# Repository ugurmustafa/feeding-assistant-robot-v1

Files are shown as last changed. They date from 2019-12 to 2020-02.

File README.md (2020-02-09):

# Feeding Assistant Robot
This repository contains all related documents and files about Feeding Assistant Robot project. This project is being held for the Senior Design Project course at Mechatronics Engineering Department at Yildiz Technical University, Istanbul, Turkey. Also, this project is advised by Prof. Erhan Akdogan at Biomechatronics Laboratory.

Currently, our team consists of four senior Mechatronics Engineering students: [Mustafa UGUR](https://www.linkedin.com/in/mustafa-uğur-41b13310a), [Oguzhan YARDIMCI](https://www.linkedin.com/in/oguzhan-yardimci-505118144), [Cemil YILMAZ](https://www.linkedin.com/in/cemil-yılmaz-664a7b13b) and [Haluk BASI](https://www.linkedin.com/in/haluk-başı-9a2321143).

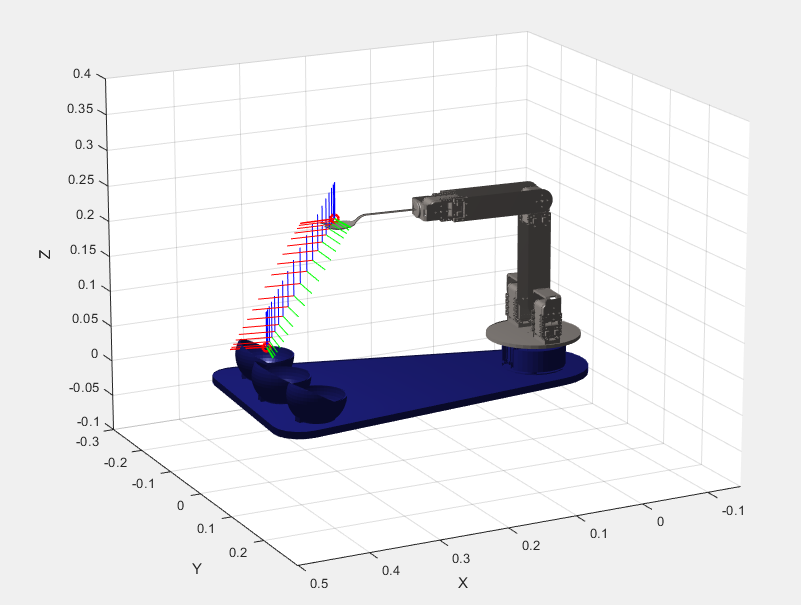
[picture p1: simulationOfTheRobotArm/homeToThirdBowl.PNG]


To see the files related with the simulation of the robot arm go to the file [simulationOfTheRobotArm](https://github.com/Ugurmustafa97/FeedingAssistantRobot/tree/master/simulationOfTheRobotArm).

To run simulation files for the trajectory planning go to  the directory [simulationOfTheRobotArm/filesForSimulation/urdf/matlabFiles/](https://github.com/Ugurmustafa97/FeedingAssistantRobot/tree/master/simulationOfTheRobotArm/filesForSimulation/urdf/matlabFiles)

To run simulation files for the dynamic analyses of the robot arm go to  the directory [simulationOfTheRobotArm/filesForController](https://github.com/Ugurmustafa97/FeedingAssistantRobot/tree/master/simulationOfTheRobotArm/filesForSimulation/urdf/matlabFiles)

To see the files realated with the mout tacking algorithm go to the file [mouthTrackingAlgorithm](https://github.com/Ugurmustafa97/FeedingAssistantRobot/tree/master/mouthTrackingAlgorithm)

To see the whole CAD files go to the [CADFiles](https://github.com/Ugurmustafa97/FeedingAssistantRobot/tree/master/CADFiles) and to see the assembly file open the file [MATLAB_feeding_robot_arm.SLDASM](https://github.com/Ugurmustafa97/FeedingAssistantRobot/blob/master/CADFiles/MATLAB_feeding_robot_arm.SLDASM)

And, to see our team final report for the fall term look the [finalReport.pdf](https://github.com/Ugurmustafa97/FeedingAssistantRobot/blob/master/finalReport.pdf) 

Please do not hesitate to contact with our team to ask anything related with the project. Please use Issues section in project's GitHub repo.

This project is supported by National Scientific and Technological Research Council of Turkey (TUBITAK) as 2209B Undergraduate Research Project Grant.

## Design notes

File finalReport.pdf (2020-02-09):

### YILDIZ TECHNICAL UNIVERSITY

### Faculty of Mechanical Engineering Department of Mechatronics Engineering

# Artificial Intelligence & Image Processing Based Feeding Assistance Robot

### Project Team

### Oguzhan YARDIMCI / 1506A023

### Mustafa UGUR / 1506A007

### Cemil YILMAZ / 15067005

### Haluk BASI / 1606A035

### Advisor Dr. Erhan Akdogan Yildiz Technical University Istanbul, Turkey

03.01.2020

SYMBOL LIST

θ
i

Joint angle [°degree
]
d
i

Link offset [mm

]
a
i

Link length [mm]
α
i

Twist angle [°degree
]
η
3

x

3

Perspective vector [

0]
δ | | | | Scaler Vector [
1

]
θ̇ | | | | Velocity [ rad
/

s
]
θ̈ | | | | Acceleration [ rad
/

s

2
]
τ | | | | Torque [kg.cm & N.m
]
F | Force r | Distance m | Mass [gr] V | Voltage

μs
Microsecond
mA

Miliampere
mAh

Miliampere

-hour
x,y,z | Coordinate Axes П | Multiplication Symbol Σ | Summation Symbol [Sigma

]
c
i | cosine [°degree] si | sine [°degree] cij | Addition of cosines [°degree

]

sij
Addition of sines [°degree ]
Px | Translational Transform Tii−1 | Transformation Matrix Dii−1 | Rotation Matrix ω | Angular Velocity v | Linear Velocity KE(R) | Rotational Kinetic Energy KE1(T) | Translational Kinetic Energy PE | Potential Energy ℒ | Lagrangian Function J | Moment of Inertia [kg ∙ m²] b | Motor viscous friction constant

[

N

∙

m

∙

s
]
Kb | Electromotive Force Constant
[

V

/rad

/

s
]
Kt | Motor Torque Constant
[

N

∙

m

/Amp
]
R | Electrical Resistane [Ω] L | Electrical Inductance [H] Kp | Proportional Controller Gain Ki

Integral Controller Gain
Kd | Derivative Controller Gain

ABBREVIATION LIST

EOG | Electrooculography
EMG | Electromyography
EEG | Electroencephalography
ALS | Amyotrophic Lateral Sclerosis
FPS | Frames per second
RGB | Red Green Blue
PLA | Polylactic Acid
ABS | Acrylonitrile Butadiene
DH | Denavit Hartenberg
FDM | Fused Deposition Modeling
DOF | Degrees of Freedom
SDK | Software Development Kit
TTL | Transistor to Transistor Logic
URDF | Unified Robot Description Format
PID | Proportional-Integrator-Derivative
Li-Po | Lithium Polymer
CAD | Computer Aided Design
USB | Universal Serial Bus
RAM | Random Access Memory
ISO | International Organization for Standardization
CE | Community Europe
IEC | International Electrotechnical Commission
R&D | Research & Development
INC | Incorporated
et. al. | et alia
mm | Millimeter
cm | Centimeter
rad | Radian
kg | Kilogram
s | Second

FIGURE LIST

Figure 1: Obi robotic feeder | 13
Figure 2: Meal Buddy robotic assist feeder | 13
Figure 3: Bestic feeding assistive device | 14
Figure 4: Tanaka et. al | 15
Figure 5: Perera et. al | 15
Figure 6: Bhattacharjee et. al | 16
Figure 7: Haarlike Features | 21
Figure 8: Haarlike in face | 21
Figure 9: The assembled model of the feeding assistance robot | 22
Figure 10: Workspace of the feeding assistance robot | 23
Figure 11: The Parts of the Feeding Assistance Robot | 24
Figure 12: Technical Drawing and Trimetric Views of the Base Plate | 26
Figure 13: Technical Drawing and Trimetric Views of the Bowl | 26
Figure 14: Technical Drawing and Trimetric Views of the Base Retainer | 27
Figure 15: Technical Drawing and Trimetric Views of the Bottom Plate | 27
Figure 16: Technical Drawing and Trimetric Views of the Connecting Holder | 28
Figure 17: Technical Drawing and Trimetric Views of the Connecting Kit | 28
Figure 18: Technical Drawing and Trimetric Views of the First Arm Link | 29
Figure 19: Technical Drawing and Trimetric Views of the Second Arm Link | 29
Figure 20: Technical Drawing and Trimetric Views of the Servo Motor | 30
Figure 21: Technical Drawing and Trimetric Views of the Wheel | 30
Figure 22: Technical Drawing and Trimetric Views of the Spoon End-Effector | 31
Figure 23: Position of the maximum torque of the robotic arm and Representation of torque distribution .......32
Figure 24: Position of the maximum torque of the robotic arm in static condition | 33
Figure 25: Dynamixel AX 18-A servo motor | 34
Figure 26: General Diagram for the control of the servo motor | 35
Figure 27: Electrical connection of the servo motor | 35
Figure 28: Coordinate frames attached to elbow manipulator | 36
Figure 29: Positions of the center of masses and link | 42
Figure 30: Rotation of the robot in x-axis(Left) , lifting in y-axis(Right) | 58
Figure 31: Flowchart of the Algorithm | 59
Figure 32: Statically Stress Analysis and Displacement Analysis of the end-effector of the robot | 60
Figure 33: Statically Stress Analysis and Displacement Analysis of the second link of the robot | 60
Figure 34: Statically Stress Analysis of the first link of the robot | 60
Figure 35: Mouth Position Determined and Shown | 61
Figure 36: Output changes when the position of the mouth is appropriate | 61
Figure 37: The interface of the Solidworks to URDF Exporter | 62
Figure 38: The robot arm in the simulation environment | 63
Figure 39: The comparison between joint space and task space solutions | 64
Figure 40: The comparison of the joint positions produced with joint space and task space for all four joints ..65
Figure 41: Angular velocity plots for each joint | 65
Figure 42: Angular acceleration plots for each joint | 66
Figure 43: End-effector with rotation on the endpoint(left), end-effector in the home position | 67
Figure 44: End-effector with rotation on top of the bowl in the right | 67
Figure 45: Simulink blocks for position control | 68
Figure 46: Comparison of input, output signals and the error between two of them for third joint | 69
Figure 47: Comparison of input, output signals and the error between two of them for second joint | 70
Figure 48: The structure in Simulink environment, which represents the robot arm | 69
Figure 49: The structure of the subsystem | 70
Figure 50: The overall system to control the robot arm | 70
Figure 51: The comparison of reference and output signals for the second joint | 71

TABLE LIST

Table 1: Comparison of Commercial Products | 13
Table 2: Comparison of academic studies | 15
Table 3: Denavit – Hartenberg Parameters Table | 16
Table 4: Specific DOF of the servo motors that were used | 24
Table 5: Denavit – Hartenberg Parameters Table of the Feeding Assistance Robot | 36
Table 6: Cost Table of the Feeding Assistance Robot | 72
Table 7: Product Backlog Items Table of the Feeding Assistance Robot | 73

ACKNOWLEDGMENT

We offer our sincere thanks to 3LS R&D CONSULTING Industry and Trade INC. for their help with the manufacturing in this project and our advisor is Assoc. Prof. Dr. Erhan AKDOGAN.

Abstract

This study explains the design of four degrees of freedom feeding assistant robot, which might be used by patients who have spinal cord injuries, amyotrophic lateral sclerosis (ALS) or Parkinson’s disease or upper-limp amputees.

The design of the robot arm was investigated deeply in the following parts of the report. First, the mechanical design of the robot arm was given in detail. After that, strength analyses of each art of the design were investigated. Then, mathematical models of the robot arm were studied, in that part forward and inverse kinematics and dynamical equations of the robot arm were calculated. In addition to these, the servo motor and the camera which was chosen for the project were explored. Next, the simulation results of the robot arm for the trajectory following were given in detail. Finally, the image processing part of the design for the mouth tracking feature of the system was explained deeply.

This project has been developed in the scope of the Mechatronic System Design course, which is served in the Mechatronics Engineering Department at Yildiz Technical University, Istanbul, Turkey.

## CONTENTS

1. Introduction | 11
1.1. The Scope and Motivation of the Project | 11
1.2. The Aim of the Project | 12
1.3. Innovative Approaches to the Project | 12
1.4. Literature for Commercial Products and Academic Studies | 12
1.4.1. Literature for Commercial Products | 12
1.4.2. Literature for Academic Studies | 15
2. Theoretical Background | 17
2.1. Analyses | 17
2.1.1. Strength Analysis | 17
2.1.2. Kinematic Analyses | 17
2.1.2.1. Forward Kinematic Analysis | 17
2.1.2.2. Inverse Kinematic Analysis | 18
2.1.3. Dynamical Analysis | 18
2.2. Image Processing | 20
3. Materials and Methods | 22
3.1. Description of the Feeding Assistance Robot Workspace | 23
3.2. Mechanical Design of the Feeding Assistance Robot | 24
3.2.1. Base Plate | 26
3.2.2. Bowl | 26
3.2.3. Base Retainer | 27
3.2.4. Bottom Plate | 27
3.2.5. Connecting Holder | 28
3.2.6. Connecting Kit | 28
3.2.7. First Arm Link | 29
3.2.8. Second Arm Link | 29
3.2.9. Servo Motor | 30
3.2.10. Wheel | 30
3.2.11. Spoon End-Effector | 31
3.3. Electromechanical Design of the Feeding Assistance Robot | 32

3.4. Analyses of the Feeding Assistance Robot | 36
3.4.1. Kinematic Analysis of the Robotic Arm | 36
3.4.1.1. Forward Kinematic Analysis of the Robotic Arm | 36
3.4.1.2. Inverse Kinematic Analysis of the Robotic Arm | 39
3.4.2. Dynamical Analysis of the Robotic Arm | 42
3.4.2.1. Defining and calculating the rotation matrices of the system | 42
3.4.2.2. Defining the angular velocities of the sequential links | 43
3.4.2.3. Calculating the angular velocities of the overall links | 43
3.4.2.4. Calculating of the Rotational Kinetic Energy | 44
3.4.2.5. Calculating the linear velocity vectors of the center of masses | 44
3.4.2.6. Calculating the translational kinetic energies of the system | 47
3.4.2.7. Calculating the potential energies of the system | 50
3.4.2.8. Calculating of Lagrangian Function | 50
3.4.2.9. Calculating the Partial Derivatives of the Lagrangian Function | 51
3.4.2.10. Calculating the Torque Values of all joints | 53
3.4.2.11. Finding Mass Matrix, C Vector and Gravity Vector | 54
3.5. Image Processing | 57
3.5.1. Flowchart of the Algorithm | 59
4. Results | 60
4.1. Results of the Strength Analysis | 60
4.2. Results of the Image Processing | 61
4.3. Results of the Simulation of the Feeding Assistance Robot | 62
5. Cost and Product Backlog Items Tables | 73
5.1. Cost Table | 73
5.2. Product Backlog Items Table | 74
6. Conclusion | 75
7. Reference | 75

### 1. Introduction

Robotic arms are one of the keystones of industrial production institutions. The robotic arm which is programmable characterize a part of the complex robot or entire of the mechanical structures. There are a lot of application areas of robotic arms like manufacturing, transportation, service or medical.

The average living time of people is increasing day by day in the world. Because of this the need for caretakers is also increasing. The use of medical robots and assistance robots to decrease these needs is becoming more and more common. In the past few years, many robots have been designed and sold in the market. Some of these designs are taking attention, especially robots that help people in their daily activities [1].

The most important group that needs care is people with physical disabilities. Even though we couldn’t find an exact number, we can say that there are almost 9 million disabled people in Turkey [2]. Many of them are suffering while they are maintaining their daily activities and need help from others. Also, we couldn’t reach the exact number of these kinds of people in Turkey. However, according to previous studies, there are 12.3 million people in the United States and 600,000 people in Japan who need assistance while doing their daily activities [3].

Eating is one of the essential activities that disabled people need to help. It is nearly impossible to do by a person who has any of the following diseases: spinal-cord injuries, strokes, upper-limb amputees or Parkinson. Because the need for a caretaker injures patient’s feelings and there isn’t enough caretaker in the market, people have been designing a few different products and selling them during the past few years.

### 1.1. The Scope and Motivation of the Project

In this study, a feeding assistance robot that has both eye-tracking and mouth-tracking methods will be performed. Users can select three different types of food without need any caretaker. Users can use this robot in hospitals and homes easily.

The feeding assistance robot can carry a spoon full of meals. The reachable area was thought 50 centimeters and created with respect to this restricted workspace. As the most important point, the robot will go to the user’s mouth smoothly and consistently.

As in the scope of Mechatronic System Design course, the part of the project includes the design of the robotic arm, analyses of the robotic arm, tests of mouth tracking part of the software, results of simulations which allows to visualize the trajectory following of the robot and the selection of servo motors and the camera with respect to simulation and analyses results.

### 1.2. The Aim of the Project

Human-Robot interaction is the most important problem in those products which are still in the market. All those products need a teaching phase that needs an external person other than the user. Besides, users must use a button or a chin stick to transmit the required commands to the system. To deal with this problem, several methods have been tried to facilitate human-robot interaction. Control using electrooculography (EOG) signals, electromyography (EMG) signals and electroencephalography (EEG) signals can be given as examples of these methods.

The project that is going to be produced will take away the teaching phase. The feeding assistance robot that goes to the established point is going to the required position by using mouth tracking. Another problem of human-robot interaction will be removed by using the eye-tracking method to select the meals. To sum, the main purpose of the system to give back their independence to the users with a robust robot arm design and easy-to-use user interface.

### 1.3. Innovative Approaches to the Project

Several feeding assistance robots were produced in the previous time. Both in industrial designs and research projects, several different methods to improve the human-robot interaction were developed and two main methods have been tried so far are the mouth-tracking and eye-tracking methods. Both the eye-tracking method and mouth-tracking algorithms were studied in the previous research projects. However, these two methods have never been used together. Our design will be the first feeding assistant robot design that uses both these two methods at the same time.

### 1.4. Literature for Commercial Products and Academic Studies

There are several products that were produced like Obi, Meal Buddy, Bestic as commercial products. Also, researchers around the world working in their research projects to develop robust feeding assistant systems and the intention in this research are is increasing constantly with the increase of the developments in the computer science field.

### 1.4.1. Literature for Commercial Products

The first known product in the feeding assistant robot market is Obi. This six degrees of freedom robot still has the biggest percentage in the market. The first Obi prototype was developed in 2006 in the United States. Obi allows users to choose between four different meals and the user can switch the meals using a touch button. It was certified like the types of ISO, CE, IEC. Obi uses a Li-Po battery as a power source (48Wh / 3.2 Ah) and eating time per full charge is 4 hours. It has portable and rechargeable properties. The weight of the Obi is 3.49 kg. Transport dimensions are 30.5 × 43.2 × 15.2 cm. The maximum and minimum food delivery heights are 38.1 cm and 5 cm, respectively [4].

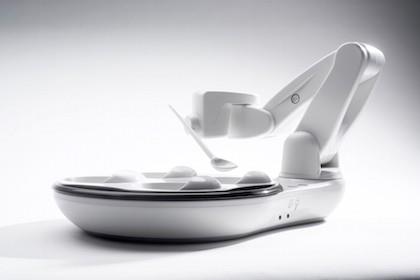
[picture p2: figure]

Figure 1: Obi robotic feeder

The second product of the feeding robot is Meal Buddy in commercial products. It has 4 DOF and 3 plates. Meal buddy has one-touch and push-button operation so it pauses anytime with a caretaker. It includes a robotic arm, a white base, three bowls, a spoon, a 2-1/2" diameter button switch and a carrying case. Bowls and base are dishwasher safe. A joystick is used to teach mouth position. Besides, joystick helps the eating program to start the feeding cycle. The caregiver can calibrate and control it easily [5].

Figure 2: Meal Buddy robotic assist feeder

The third one of the commercial products is Bestic. it has four degrees of freedom and a single plate. Bestic has an adjustable arm with a spoon on the end-effector. The motion of the arm can be controlled by the user through a button that could be pressed by hand, knee, foot, chin or shoulder. The height and distance of the end-effector to the mouth can be adjusted. The user has possibilities to change the user steers with different control methods. The spoon does not enter the mouth for safety. The weight of Bestic is 2 kg and the sizes are 3.4 x 8.7 x 7.9 incℎes. Eating time with batter is approximately 5 hours [6].

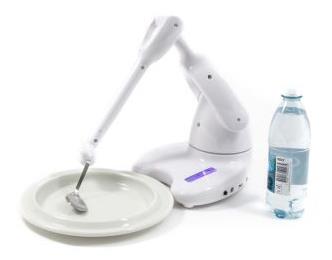
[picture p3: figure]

Figure 3: Bestic feeding assistive device

Table 1: Comparison of Commercial Products
| Robot Name Features | Obi Robotic Feeder | Meal Buddy Robotic Assist Feeder | Bestic Feeding Assistive Device | Our Feeding Robot
Human-Robot Interface | Eye Tracking | | | | ✓
| Push Buttons | ✓ | ✓ | ✓ | ✓
| Joystick | | ✓ | ✓
| Head Control | | | ✓
| Chin Movements
How to reach to the user? | Teaching Phase | ✓ | ✓
| Mouth Tracking | | | | ✓
Mechanical Design | 4 - DOF | | ✓ | ✓ | ✓
| 6 - DOF | ✓
Serving | Single Plate | | | ✓
| 3 Plate | | ✓ | | ✓
| 4 Plate | ✓
Usability | Easy to Transport | ✓
| Cost | $5950 | $3500 | $3900 | $650

### 1.4.2. Literature for Academic Studies

One of the academic works is the project that was developed by Tanaka et.al. Ultrasonic motors were used in this robot design to make it silent and to be less harmful to the electronic devices around the robot. In this study, the robot was designed to be controlled with an eye-tracking interface. The design does not include a multi-jointed arm structure. Therefore, the end-effector just moves in one direction [1].

Figure 4: Tanaka et. al.

The second one is four degrees of freedom robot that was produced by Perera et. al. This meal assistance robot that is controlled by using Electroencephalography (EEG) signals by users. And, it could track the position of the mouth and could detect whether the mouth is open or not. Moreover, the end-effector can reach to user’s mouth because of the differences in seating positions using the mouth position tracking method [7].

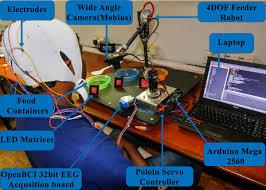
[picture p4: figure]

Figure 5: Perera et. al.

The third study was made by Bhattacharjee et. al. This design has six degrees of freedom robot arm and the movements of end-effector are done by finding the mouth position of the user. Detection of open and closed mouth is made to be understandable and there is a fork as an end-effector instead of a spoon [3].

Figure 6: Bhattacharjee et. al.

Table 2: Comparison of academic studies
| Robot Name Features | Tanaka et. Al | Perera et. Al. | Bhattracharjee et. Al. | Our Feeding Robot
Human-Robot Interface | Eye Tracking | ✓ | | | ✓
| Push Buttons | | | ✓ | ✓
| EEG Signals | | ✓ | ✓
How to reach to the user? | Teaching Phase
| Mouth Tracking | | ✓ | ✓ | ✓
Mechanical Design | One direction | ✓
| 4 - DOF | | ✓ | | ✓
| 6 - DOF | | | ✓
| End-Effector Type | Spoon | Spoon | Fork | Spoon
| Easy to transport | | | | ✓
Serving | No Plate | ✓
| Single Plate | | | ✓
| 3 Plate | | ✓ | | ✓

### 2. Theoretical Background

In this title of the report, theoretical backgrounds of analyses and image processing were explained. These topics were covered in an order that first strength analyses were covered briefly. Then forward and inverse kinematic analyses were given. Finally, the dynamical analysis topic was described briefly.

### 2.1. Analyses

This title is separated into three subtitles. First one of them is strength analysis using Solidworks and ANSYS. The second one is kinematic analyses of robot arms. The third one is the dynamical analysis of robot arms.

### 2.1.1. Strength Analysis

The mechanical components can be analyzed using Solidworks and ANSYS. The most important point of the analysis is to obtain the best mesh analysis because the process can take a long time. In the fine-tuning, the program can make an analysis of the system. In the coarse tuning, the program can make analysis faster than fine-tuning, but the results might not be sufficient. The relationships of overall components have to be defined and there should not be a limitation between parts.

### 2.1.2. Kinematic Analyses

The problem of kinematics is used to define the motion of the manipulator without considering of forces and torques. Denavit-Hartenberg representation, which is a general transformation between two joints, requires four parameters. These parameters, known as the Denavit-Hartenberg (DH) parameters which became a standard to describe robot kinematics. In serial robots, to calculate the forward kinematics is easier than inverse kinematics. In parallel robots, to calculate inverse kinematics is easier.

### 2.1.2.1. Forward Kinematic Analysis

The transformation of the coordinate of the end-effector point from the joint space to the world space is known as forward kinematic transformation. It is also called more clearly, forward kinematic which is to determine the position and orientation of the end effector given the values for the joint variables of the robots [9].

Table 3: Denavit – Hartenberg Parameters Table

Denavit – Hartenberg (DH) method uses the four parameters including ai

,αi

, di and θi
;
which are the link length, twist angle, link offset and joint angle, respectively. Joint Angle and Link Offset are joint parameters. Link Lengtℎ and Twist Angle are link parameters.
Axis Number i | Link Length ai | Twist Angle αi | Link offset di | Joint angle θi
1 | a1 | α1 | d1 | θ1 ∗
2 | a2 | α2 | d2 | ∗ θ2

- θi

, the joint angle is the angle from xi−1 to xi measured around the zi−1.
- di

, the link offset is the distance from Oi−1 to Oi measured along zi−1.
- ai

, the link length is the distance from zi−1 to zi measured along xi
- αi
, the twist angle is the angle from zi−1 to zi measured along xi

The matrix Ti

i−1
is known as a D-H convention matrix given in this equation. In the matrix Ti

i−1
, it means the homogenous transformation matrix, the quantities of ai−1,αi−1, di are constant for a given link while the parameter θi for a revolute joint is
variable.

Ai = Ti

i−1 =[

cosθi
sinθi
0
0

### −cosαisinθi cosαicosθi

sinαi
0
sinαisinθi | ai cosθi
−sinαicosθi | ai sinθi
cosαi | di
0 | 1

]

Ai = Ti

i−1 = P = [
R3×3

px
py
pz
η3×3 | 1

]

- r3x3 = Rotational Transform: Rotational Transformation between the tool coordinate frame and the base coordinate frame.
- p3x3 = Translational Transform: Translational Position of x,y,z axes of the tooltip with respect to the base.
- η3x3 = Perspective Vector: Always 0.
- δ = Scaler Vector: Always 1.

### 2.1.2.2. Inverse Kinematic Analysis

The transformation of coordinates from world space to joint space is known as inverse kinematics transformation. The inverse kinematics solution uses the position and orientation (Px, Py, Pz

) of the robot’s end-effector to solve the joint angles (θ1, θ2, θ3, …).

### 2.1.3. Dynamical Analysis

The dynamics equations are used to describe the motion of the manipulator with considering of forces and torques. The equations of motion are important to consider in the design of robots, in simulation and animation of robot motion and in the design of control algorithms.

Dynamical analysis can be made using two methods. The first one of them is Euler Lagrange equations, it means Lagrangian Formulation, describes the evolution of a mechanical system subjected to holonomic constraints. In order to determine the Euler-Lagrange equations in a specific situation, one has to form the Lagrangian of the system, which is a difference between the kinetic energy and potential energy. The second one is Newton-Euler Formulation which is a recursive formulation of the dynamic equations that is often used for numerical calculation [8].

Forward Dynamics: Given θ, θ̇

, τ and find θ̈
Inverse Dynamics: Given θ, θ,

̇ θ̈and find τ

The Forward dynamics problem is to calculate the joint accelerations θ̈, given the current joint positions θ, the joint velocities θ̇
, and the forces and torques τ applied at each joint. The forward dynamics is useful for simulation. The inverse dynamics problem is to find the joint forces and torques τ needed to create the acceleration θ̈ for the given joint positions and velocities that are θ, θ̇ respectively. The inverse dynamics are useful in the control of robots. Robot dynamics is necessary not just for simulation and control but also for the analysis of robot motion planners and controller.

In this study, Lagrangian Formulation was selected to make dynamical analysis because it is easier than Newton-Euler Formulation. In the Lagrangian Formulation that is based on the differentiation energy terms with respect to the system’s variables and time, the Lagrangian Function is founded to calculate the torque values of each joint.

L( θ, θ̇ ) = K( θ, θ̇ ) − P(θ)

which is K( θ, θ̇ ) is Kinetic Energy of the System and P(θ) is Potential Energy of the System.

The vector of joint forces and torques can be demonstrated as follows:

Fi =

d
dt (

∂L
∂ẋi

) −

∂L
∂xi
, | τi =

d
dt (

∂L
∂θ̇
i

) −

∂L
∂θi

which is the meaning of ℒ is the Lagrange function of joint variables in the Euler Lagrange equation.

These equations are rather complicated even for simple 2R robots. Some terms are linear in the joint acceleration θ̈. Some terms do not depend on the joint acceleration but instead depend on a product of joint velocities like θ̇
3

2 or θ̇
3

2
| . Some terms have no dependence on
the joint velocities or accelerations. With this observation, the vector equation of motion can be written as follow:

τ = M(θ)θ̈+ c(θ, θ̇) + g(θ)

which is M matrix is called the mass matrix. C vector includes velocity-product term since it composed of terms with θ̇
i

2
in it. Vector g is the gravity vector term since it depends on gravity. It is called a gravity term under the assumption that the potential energy comes only from gravity but if there are springs at the robot joints, those springs would also contribute to the potential energy and therefore g(θ).

Overall these equations look like f = ma + gravity which is ma is equal to tℎe M(θ)θ̈+ c(θ, θ̇) and gravity is equal to tℎe g(θ) except that the accelerations of the masses depend on the joint accelerations but also products of the joint velocities. These velocity-product terms are appeared because of the joint coordinates are not inertial coordinates.

τ = M(θ)θ̈+ c(θ, θ̇) + g(θ) + J
T(θ)Ftip

There is one more term added to the right-hand side which is J

T
(θ) is Jacobian
tranpose and Ftip is wrencℎ tℎat tℎe end effector applies to the environment.

When we focus on the velocity-product terms, it means “vector c”, terms that have the square of a single joint velocity are called Centripetal terms( θ̇
i

2
) and terms that have a
product of two different joint velocities are Coriolis terms( θ̇

i θ̇
j).

### 2.2. Image Processing

First of all, the frame rate which is one of the most important for image processing is selected. The sensor speed is the speed at which a camera takes the image and delivers it to the system. It should not be considered as focusing and zooming speeds. The sensor speed is expressed by the number of frames and exposure time it produces per second(FPS). The more frames a camera shoots in a second, the more detail it can turn into a signal. [19]

When the sensor wants to convert the movement of an object relatively faster to the number of frames it can produce, any point of the object creates a color value on any point on the sensor before the processing of that mouse falls on the neighbors of that sensor point, causing the image to be blurred. It is important to be able to shoot frames very quickly, but the key point is whether all frames produced in one second have the correct color values.

The movements in our system will not be very fast and 30 FPS will suffice for our system as observed in other projects for such purposes.

The logic of the gray filter is to assign a single value to the pixels by averaging the 3 basic color values which are red, green blue (RGB, [0-255 0-255 0-255]) found in the pixels. Gray filter was applied by using the OpenCV library.

HaarCascade is a system identified by a scientist named Alfred Haar. A method used to locate objects on an image. This method is called Haarlike features. The explanation of the Haarlike is given as follow:

Edge Feature: Indicates an edge property if a certain area on the image consists of a dark area and a certain area consists of light colors.

Line feature: If the image consists of open, closed, light colors respectively, there is a line feature.

Four-Square Feature: If there are diagonally dark and light tones diagonally as crosswise, it refers to the four-square feature.

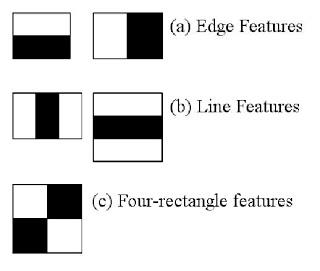
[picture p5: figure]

Figure 7: Haarlike Features

Using Haarlike features that are shown in Figure 7, many objects can be identified in the image such as lines, edges, faces, eyes, vehicles, etc. HaarCascade is applied to a human face as is shown in Figure 8. The HaarCascade method has been trained many times in advance and knows how the face shape is. When introducing a flower recognition or plate recognition process, the plate is defined many times. For example, in Figure 8, a system that seeks a face-first search for two eyes. If there is an eye, it will look for a nose. The nose is the structure that gives the desired results by checking whether there is an eyebrow.

Figure 8: Haarlike in face

The item can be defined and searched for objects in the image using HaarCascade, which means HaarCascade can be made independently.

### 3. Materials and Methods

In this study, a 4 DOF artificial intelligence and image processing based feeding assistance robotic arm for disabled people was developed which is shown schematically in 8. The presented robotic arm is composed of the serial link which is affixed to each other with revolute joints from the base frame to the end-effector. All components were designed, assembled and analyzed by using Solidworks. Forward and inverse kinematic analysis were developed by using Denavit-Hartenberg parameters. Dynamic components were analyzed by using the standard mechanical formula and Solidworks. The feeding assistance robot will be attached to people.

As a material selection, all components were manufactured from PLA (Polylactic Acid) due to the properties of this organic biopolymer and thermoplastic material. It is not harmful to people’s health. When we compare with ABS, PLA has a sleekier surface. 3D Printer using FDM technology can print PLA properly. The specifications of PLA are as follow:

- Hard structure. Therefore, PLA is durable and resistant to impacts.
- Slight flexibility but some brittle.
- No problems with plastic deformation during the cooling process.
- Resistance to temperature.
- Difficult to dissolve with acetone.
- Very easy to print according to ABS.

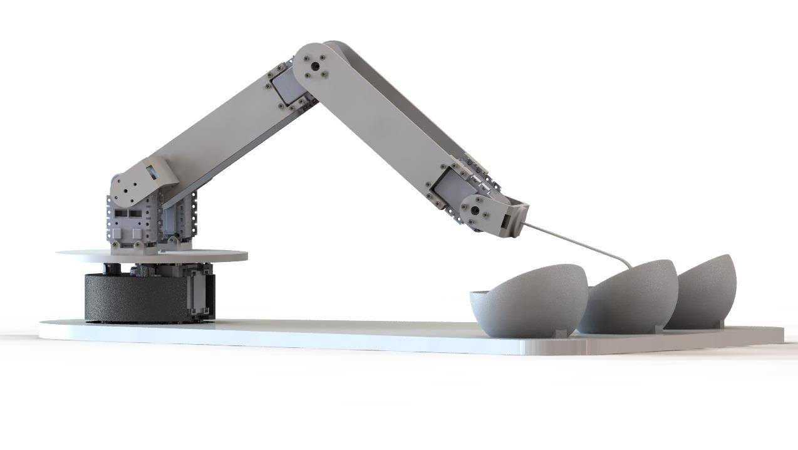
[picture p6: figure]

Figure 9: The assembled model of the feeding assistance robot

Figure 10: Workspace of the feeding assistance robot

### 3.1. Description of the Feeding Assistance Robot Workspace

The workspace of a manipulator is the total volume swept out by the end effector as the manipulator executes all possible motions. The workspace is constrained by the geometry of the manipulator as well as mechanical constraints on the joints. For example, a revolute joint may be limited to less than a full 360° of motion. The workspace is often broken down into a reachable workspace and a dexterous workspace. The reachable workspace is the entire set of points reachable by the manipulator, whereas the dexterous workspace consists of those points that the manipulator can reach with an arbitrary orientation of the end effector. Obviously, the dexterous workspace is a subset of the reachable workspace. In shortly, the robot workspace or reachable spaces consist of all the points in the Cartesian space that the end effector of the robotic arm can access. The workspace and quick access to a certain point in all robotic arms are strongly dependent on linkage properties, joint properties (length, angles, angular velocity, and torque), degree of freedom, angle/translation limitations and robot configurations.

Consider the feeding assistance robot in Figure 10. The right side shows the complete work envelope of the robot from the side view. The left side of Figure 10 shows the whole workspace from the top view. The maximum longitudinal distance reached by the arm is 45.826 cm. All dimensions have a tolerance in the range of 2–4 mm. The maximum height of the accessible point is 50.176 cm. According to the reachable points, the sizes of the feeding assistance robot is sufficient to be used in medical applications. In shortly, the workspace of the feeding assistance robot has a suitable reach to the user’s mouth and bowls easily [9].

### 3.2. Mechanical Design of the Feeding Assistance Robot

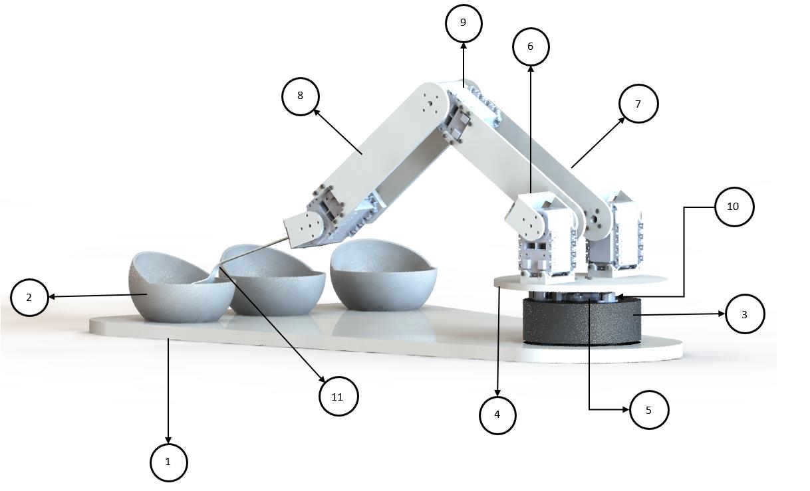
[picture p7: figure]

The robot arm parts could be seen in figure 11 and the name of each part is given below:

1. Base Plate
2. Bowl
3. Base Retainer
4. Bottom Plate
5. Connecting Holder
6. Connecting Kit
7. First Arm Links
8. Second Arm Links
9. Servo Motor
10.Caster Wheel
11.Spoon End-Effector

In this section, how to design a robot arm and robot arm parts’ specifications subjects are worked.

The mechanical design of the robot arm is based on a robot manipulator with similar functions to a human arm. Robotic arm system often consists of links, joints, actuators, sensors, and controllers. The links are connected by joints to form an open kinematic chain. One end of the chain is attached to the robot base plate which has two servo

Figure 11: The Parts of the Feeding Assistance Robot motors connection points, and another end is equipped with a spoon manipulator. The links of the manipulator are considered to form a kinematic chain. In a robotic system, the number of degrees of freedom is determined by the number of independent joints. Complexity and cost are increased as a number of degrees of freedom. In our robotic arm design with only four degrees of freedom is designed because it is enough for most of the necessary movement. Specification of each joint is given below:

Table 4: Specific DOF of the servo motors that were used
Degree Of Freedom | Rotation Degree | Servo Motor
1 2 3 4 | 300° 180° 180° 90° | Dynamixel AX-18A 2×Dynamixel AX-12A Dynamixel AX-18A Dynamixel AX-12A

In the second joint, two Dynamixel AX-12A servo motors are used to increase torque value and to decrease the cost.

The area that the spoon end-effector can reach is called robot arms workspace. The degree of freedoms, arm link lengths, translation limitations, and robot configuration affect the robot arm workspace. So, keeping all these things in mind, the assistant robot arm is designed considering these configurations based on the previous design.

In this process steps that are given below are carried out:
- The number of degrees of freedom is determined.
- The workspace of our robot arm is determined similar to a human arm and it could be seen in figure 10.
- The arm link lengths and the spoon manipulator length are determined based on motor-torque calculations and academicals design and these parts could be seen in figures 18,19 and 22.
- The length of other parts of our design is determined based on the specification of the servo motors. These are:
- Base Retainer
- Bottom Plate
- Connecting Holder
- Connecting Kit also these parts could be seen in figures 14,15,16 and 17.
- The base plate is designed based on the workspace and this part could be seen in figure 12.
- The bowl is designed to operate the robot arm effectively and to gain an aesthetic appearance to our system and this part could be seen in figure 13.
- The assembly of our design is completed to realize the static analysis and simulation of our robot arm.

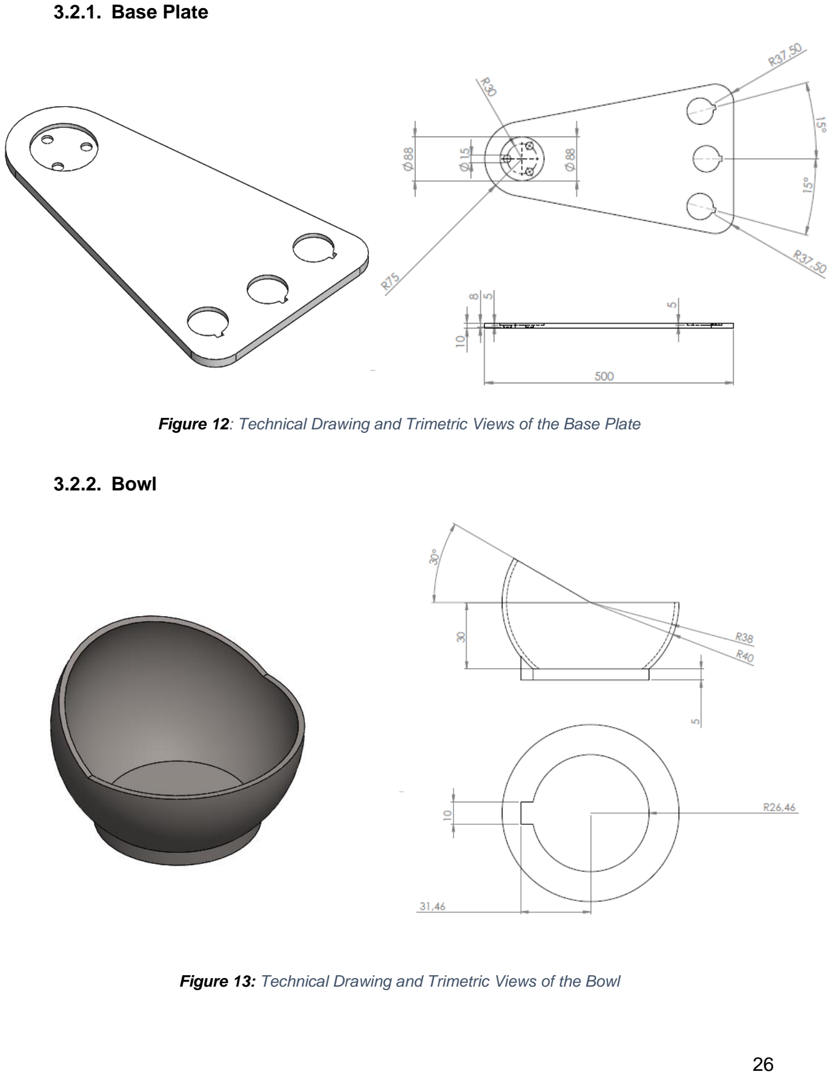
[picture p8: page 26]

### 3.2.1. Base Plate

### 3.2.2. Bowl

Figure 12: Technical Drawing and Trimetric Views of the Base Plate

Figure 13: Technical Drawing and Trimetric Views of the Bowl

### 3.2.3. Base Retainer

### 3.2.4. Bottom Plate

Figure 14: Technical Drawing and Trimetric Views of the Base Retainer

Figure 15: Technical Drawing and Trimetric Views of the Bottom Plate

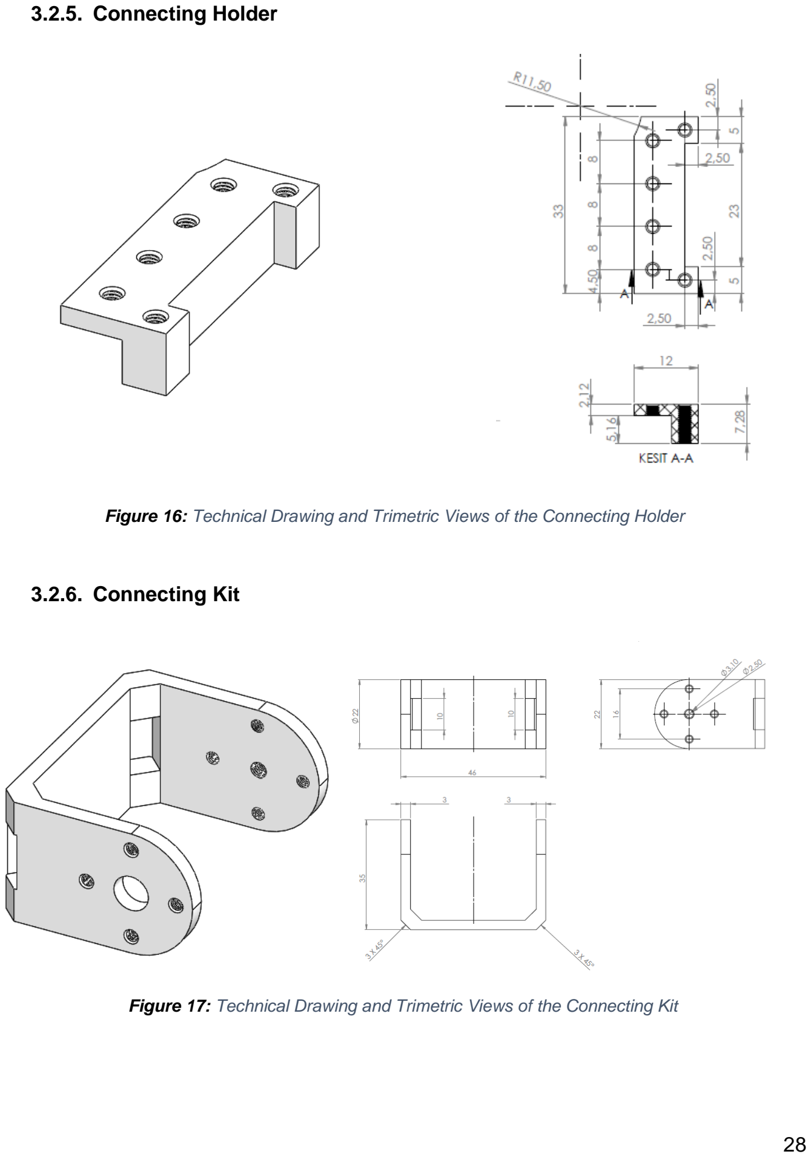
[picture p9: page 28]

### 3.2.5. Connecting Holder

### 3.2.6. Connecting Kit

Figure 16: Technical Drawing and Trimetric Views of the Connecting Holder

Figure 17: Technical Drawing and Trimetric Views of the Connecting Kit

### 3.2.7. First Arm Link

### 3.2.8. Second Arm Link

Figure 18: Technical Drawing and Trimetric Views of the First Arm Link

Figure 19: Technical Drawing and Trimetric Views of the Second Arm Link

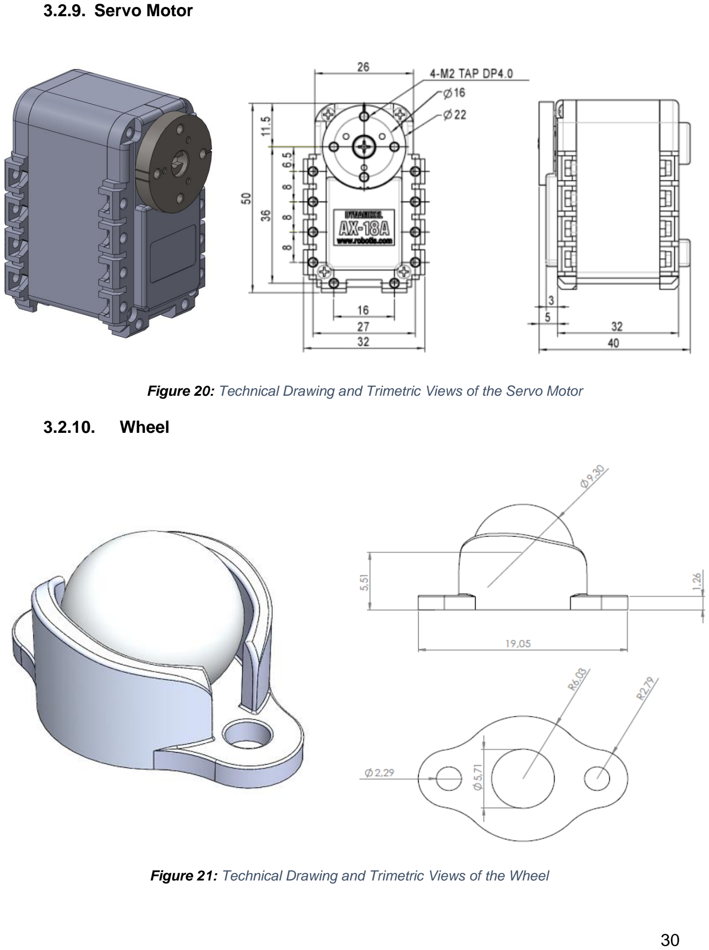
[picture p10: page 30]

### 3.2.9. Servo Motor

### 3.2.10. Wheel

Figure 20: Technical Drawing and Trimetric Views of the Servo Motor

Figure 21: Technical Drawing and Trimetric Views of the Wheel

### 3.2.11. Spoon End-Effector

Figure 22: Technical Drawing and Trimetric Views of the Spoon End-Effector

### 3.3. Electromechanical Design of the Feeding Assistance Robot

In the selection of servo motors, some technical requirements were considered. In the following of this part of the report, these requirements and detailed explanations about how the selected servo motor satisfies them will be given. Also, there are some factors other than technical requirements, and these are cost, reliability, availability, and difficulty of the control of the motor. This factor also will be explored in the following document.

The first technical requirement that our system must satisfy that our system should be able to move smoothly, which guarantees that the movement of the spoon (which is also our end-effector) without spilling out the food on it. In order to meet this requirement, the servo motor must have a small resolution. It could be verified from the values that were reached in simulations. For example, the mean value of the change in the second joint during the trajectory following from the home position to the bowl in the middle was 0.0108 rad which is equal to 0.62 degrees. From this evaluation, it could be easily seen that our servo motor in the second joint must have a smaller resolution than 0.62 degrees. To provide this smooth trajectory following the servo motors also have to have a small response time. It could be confirmed from the simulation, the system works properly when 0.02 s was chosen as the interval time between two different trajectory points. So servo motors must have a smaller response time than 0.02 s. Another thing that our servo motors have to maintain was that these motors should be able to feedback some values to our system. For example, shaft position, speed, and load. These values will provide to our robot arm to keep a convenient movement around its workspace.

Secondly, our system must sustain the user’s confidence and maintain a safe operation. In order to ensure these, our system has to follow trajectories smoothly without any sudden movement, this requirement was talked in the above immensely, also it should have collision detection. This collision detection feature could be added to our system with servo motors that could feedback the load value.

Other than these technical requirements our servo motors must maintain required torque values both in static conditions and dynamic conditions. The static condition of the robot arm and required torque values are stated in Figure 24. The dynamic conditions were explored in the next chapters in this report.

Figure 23: (a) Position of the maximum torque of the robotic arm (b) Representation of torque distribution on the robotic arm

As shown in Figure 23, the orientation of the robot must be like that to obtain maximum torque in each link and joints because of the minimize of the cosine angle of joints. Maximum Torque will be in the farthest point because of the torque formula which is

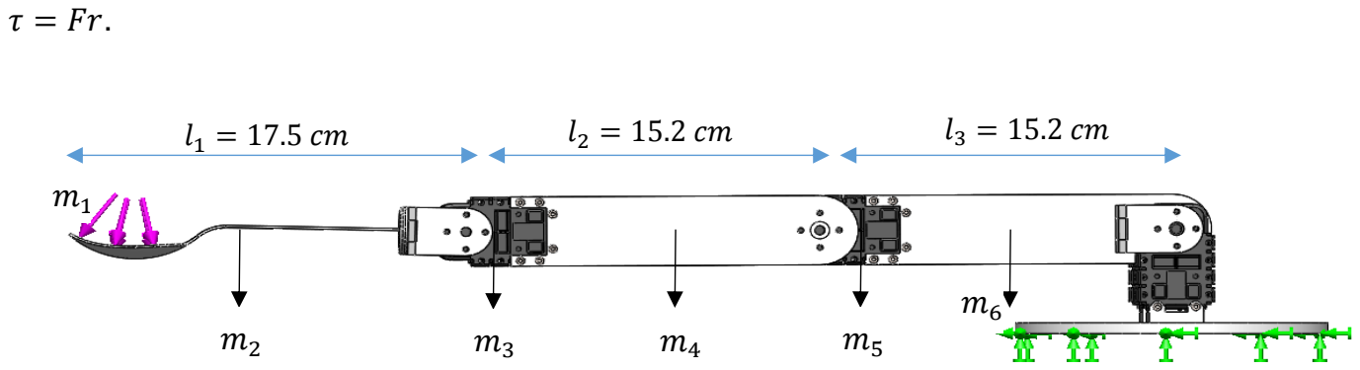
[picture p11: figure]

Figure 24: Position of the maximum torque of the robotic arm in static condition

m1 = 0.06 gram | m2 = 9.59 gram | m3 = 58 gram
m4 = 14.24x2 gram | m5 = 58 gram | m6 = 12.59x2 gram

While finding the maximum torque value of the last joint, the load being lifted and the mass of the end-effector are taken into account. Mass of the end-effector is equal to 9.59 grams and the load being lifted is equal to 6 grams. Otherwise, the length of the end-effector is equal to 17.5 cm.

τ1 = m1

l1 + m2

l1
2
| = 6x10⁻³x17.5 + 9.59x10⁻³x

17.5
2
| | = 0.1889125 kgcm

In the second joint, the mass of link 2 is equal to 14.24 grams and the mass of the servo motor is equal to 58 grams. And, the length of the second link is equal to 15.2 cm.

τ2 = m1 | (l1 + l2 ) + m2 ( l1
| 2 +l2) + m3
l2 + m4

l2
2

6x10⁻³x(17.5 +15.2) + 9.59x10⁻³x (

17.5
2

+ 15.2) + 58x10⁻³x15.2+ 14.24x10⁻³x

| | 15.2
| | 2 = 1.524 kg cm

In the first joint, the mass of link 3 is equal to 12.59 grams and the mass of the servo motor is equal to 58 gr. And, the length of the first link is equal to 15.2 cm.

τ3 = m1

(l1 + l2 + l3

)+ m2 (

l1
2

+ l2 + l3)+ m3
(l2 + l3

)+ m4 (

l2
2

+ l3)+ m5
l3 + m6

l3
2

= 4.148 kgcm

where τ1, τ2, τ3 are torque values required for those joints. In this analysis, the torque value required for the first joint wasn’t calculated because there is no torque affects the rotation of this joint.

In addition to these technical requirements, our servo motors must be user-friendly. This means that the user should be able to control the motor easily. Some servo motors exist in the market were investigated. In sum, it was decided that a servo motor that has its own Software Development Kit (SDK) in which the user controls it with any programming language must be used in our robot arm.

In the above, technical requirements and features that our servo motors must have to satisfy these technical requirements were explained in detail. In the following parts, the servo motor that we used in our project will be investigated.

The Dynamixel AX18-A servo motor was chosen for our project. It provides feedback on shaft position, speed, temperature, voltage and load values. It has its own SDK which enables us to control the robot. This SDK is compatible with many of the programming languages like C++, Python, and Matlab, and one could control this servo motor just a couple of lines of Python code. One other advantage of this motor is that it does not need an extra circuit like a servo controller, it just needs a USB to TTL converter and 11.1 V power supply. Finally, as could be seen in figure 20, it also has many connection points and a nice case.

Figure 25: Dynamixel AX 18-A servo motor

As we mentioned in the above, the servo motor has to be chosen such that it has a resolution lower than 0.62 degrees. However, the servo motor has a resolution 0.29 degrees which is pretty enough for our system.

Also, the response time requirement was talked about. And, it was decided that the motor must have a response time lower than 0.02 s. In our case, the servo motor’s response time is 0.254 μs. It means that our servo motor could perform different actions in 0.254 μs and this is pretty enough for our system.

Other than these specifications it has a compatible size and weight with our robot arm design. The size of the motor is 32 × 50 × 40 mm while the weight is 54.5 gram. Especially, the lightweight specification of the servo motor made our joint designs more efficient.

The final feature of the servo motor that it could be easily connected to the computer as it could be seen in figure 26. Which enables us to control the motor easily. In addition to this, there is no need for a voltage regulator, and it could be used with connecting the power cable from the power source as it is seen from the figure 27, in our case the power source was 11.1 V 3S Lipo battery from ProFuse brand.

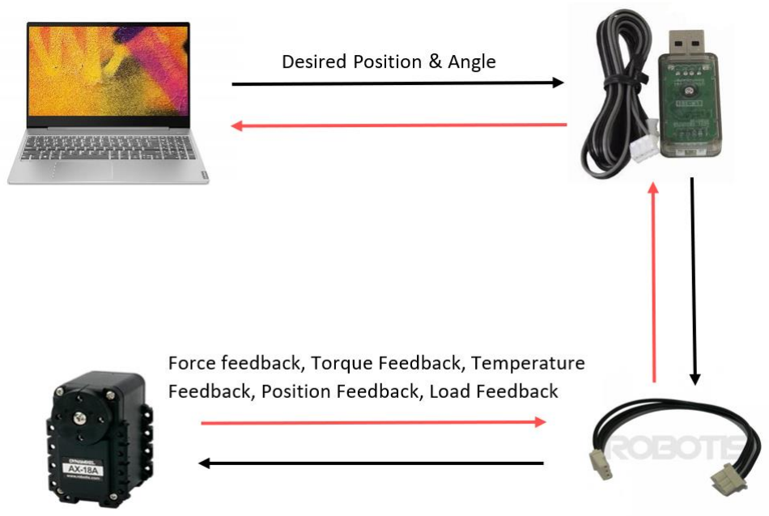
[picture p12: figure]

Figure 26: General Diagram for the control of the servo motor

Figure 27: Electrical connection of the servo motor

Our servo motor’s maximum current is 2200 mA and none of the servo motors in our system work with above the half of this value. This means that our servo motors use a maximum of 1100 mA with their current radial speeds and loads. According to these assumptions working time could be determined from the following equations:

Battery time(ℎours) =

Battery Capacity(mAℎ)
Current(mA)

× 0.707

=

2800 mAℎ
4400 mAℎ

× 0.0707 = 0.44 ℎours

To sum, our servo motors are quite suitable for our project with its high technical specifications, its SDK, and its plugin connection type. All of these give us a huge advantage of the testing of the robot arm to make our system more robust.

### 3.4. Analyses of the Feeding Assistance Robot

In this title of the report, Analyses of the Feeding Assistance Robot will be mentioned. The background information about the analyses was given in the previous section.

### 3.4.1. Kinematic Analysis of the Robotic Arm

The kinematic equations of the robot that has 4 DOF were founded. In forward kinematics, Denavit – Hartenberg Parameters were used. In inverse kinematics, the standard trigonometric formula was used.

### 3.4.1.1. Forward Kinematic Analysis of the Robotic Arm

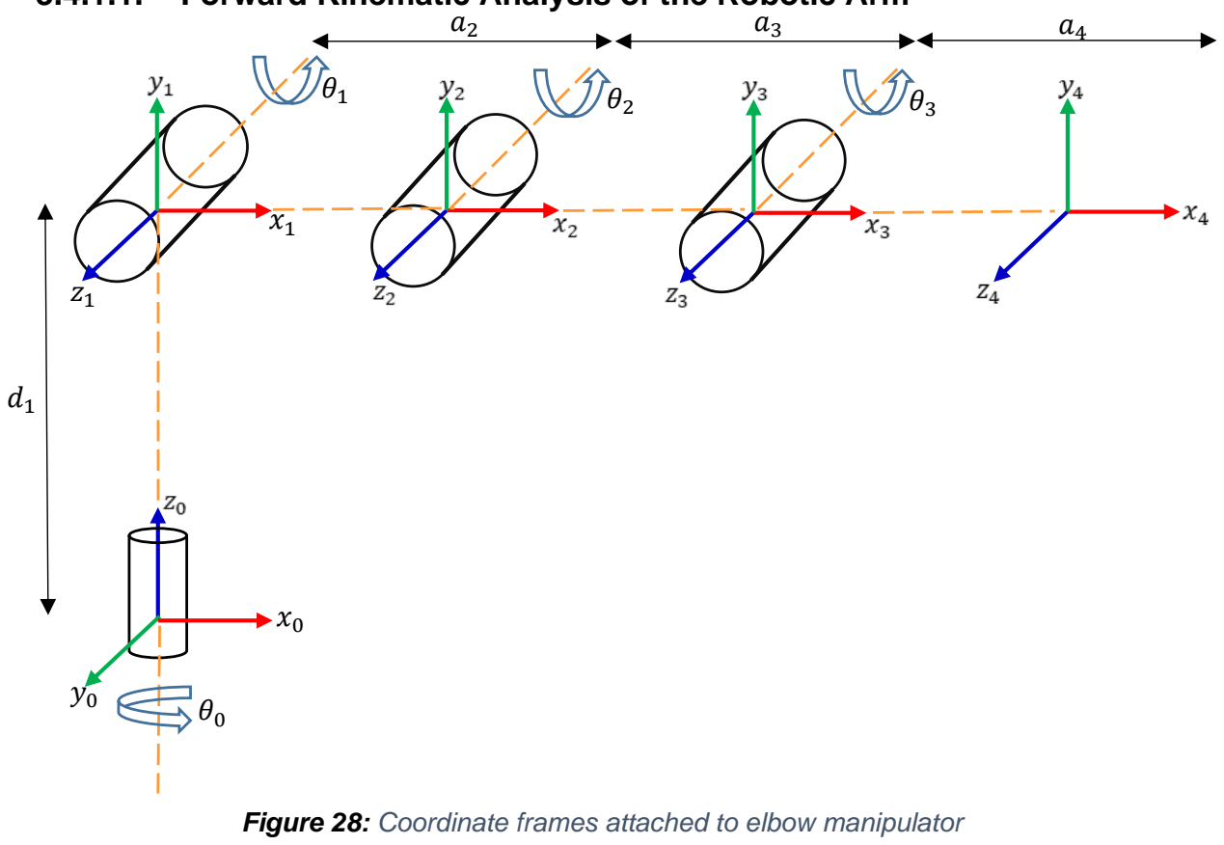
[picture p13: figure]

In Figure 28, coordinate frames are demonstrated. zi axes are selected because of the motion axis which is revolute joints. xi axes are selected to be perpendicular to zi−1 and zi
. Hereby, the Denavit – Hartenberg (D-H) Parameters were obtained as follow:

Figure 28: Coordinate frames attached to elbow manipulator

Table 5: Denavit – Hartenberg Parameters Table of the Feeding Assistance Robot

By using D-H Parameters, the homogenous transformation matrices are obtained.

A1 = T1

0 = [

cosθ1 | 0 | sinθ1 | 0
sinθ1 | 0 −cosθ1 | 0
0 | 1 | 0 | d1
0 | 0 | 0 | 1

]

A2 = T2

1 = [

cosθ2 | −sinθ2 | 0 | a2 cosθ2
sinθ2 | cosθ2 | 0 | a2sinθ2
0 | 0 | 1 | 0
0 | 0 | 0 | 1

]

A3 = T3

2 = [

cosθ3 | −sinθ3 | 0 | a3 cosθ3
sinθ3 | cosθ3 | 0 | a3sinθ3
0 | 0 | 1 | 0
0 | 0 | 0 | 1

]

A4 = T4

3 = [

cosθ4 | −sinθ4 | 0 | a4 cosθ4
sinθ4 | cosθ4 | 0 | a4sinθ4
0 | 0 | 1 | 0
0 | 0 | 0 | 1

]

Then, the arm matrix is created by multiplying each matrix. T4

0 matrix defined as follows,

T4

0 = ∏ Ti

i−1 =
4
i=1 | T1

0 T2
1 T3

2 T4

3 = [

r11 | r12 | r13 | r14
r21 | r22 | r23 | r24
r31 | r32 | r33 | r34
r41 | r42 | r43 | r44] = A1A2A3A4
Axis Number i | Link Length ai | Twist Angle αi | Link offset di | Joint angle θi
1 | 0 | π/2 | d1 | ∗ θ1
2 | a2 | 0 | 0 | ∗ θ2
3 | a3 | 0 | 0 | ∗ θ3
4 | a4 | 0 | 0 | θ4 ∗

r11 = c1c4c23 − c1s4s23 = cos(θ2 + θ3 + θ4)cos (θ1) r12 = −c1s4c23 − c1c4s23 = −sin(θ2 + θ3 + θ4)cos (θ1) r13 = s1
r14 = a2c1c2 + a4c1c4c23 − a4c1s4s23 + a3c1c23
r21 = c4s1c23 − s1s4s23 = cos(θ2 + θ3 + θ4

) sin(θ1)
r22 = −s1s4c23 − c4s1s23 = −sin(θ2 + θ3 + θ4)sin(θ1) r23 = −c1
r24 = a2c2s1 + a4c4s1c23 − a4s1s4s23 + a3s1c23
r31 = c4s23 + s4c23 = sin(θ2 + θ3 + θ4)
r32 = c4c23 − s4s23 = cos(θ2 + θ3 + θ4)
r33 = 0
r34 = d1 + a2s2 + a4c4s23 + a4s4c23 + a3s23 r41 = 0
r42 = 0
r43 = 0
r44 = 1

In the expressions of these elements of the arm matrix, the variables are defined as follow:

ci = cosθi

, si = sinθi

, cij = cos(θi + θj) , sij = sin(θi + θj)

And arm matrix ( T4

0
) consist of as indicated:

⇒ [

c234c1
c234s1
s234
0

−s234c1
−s234s1
c234
0
s1 | a2c1c2 + a4c1c4c23 − a4c1s4s23 + a3c1c23
−c1 | a2c2s1 + a4c4s1c23 − a4s1s4s23 + a3s1c23
0 | d1 + a2s2 + a4c4s23 + a4s4c23 + a3s23
0 | 1

]

It is possible to define the values of the translational transform (Px, Py, Pz ) with respect to
the base coordinate system by using arm matrix.

Px = a2cosθ1cosθ2 − a4cosθ1cosθ4

(sinθ2sinθ3 − cosθ2cosθ3

)

−a4cosθ1sinθ4

(cosθ2sinθ3 + cosθ3sinθ2

) + a3cosθ1(cosθ2cosθ3 − sinθ2sinθ3)

Py = a2cosθ2sinθ1 − a4cosθ4sinθ1

(sinθ2sinθ3 − cosθ2cosθ3

)

−a4sinθ1sinθ4

(cosθ2sinθ3 + cosθ3sinθ2

) + a3sinθ1

(cosθ2cosθ3 − sinθ2sinθ3

)

Pz = d1 + a2sinθ2 + a4cosθ4

(cosθ2sinθ3 + cosθ3sinθ2

) + a4sinθ4

(cosθ2cosθ3 −
sinθ2sinθ3

) + a3(cosθ2sinθ3 + cosθ3sinθ2)

Also, the arm matrix can be demonstrated more clearly as follow:
[

c234c1
c234s1
s234
0

−s234c1
−s234s1
c234
0
s1 | c1(a3c23 + a2c2 + a4c234)
−c1 | s1(a3c23 + a2c2 + a4c234)
0 | d1 + a3s23 + a2s2 + a4s234
0 | 1

]

### 3.4.1.2. Inverse Kinematic Analysis of the Robotic Arm

The elements of translational transform (Px, Py, Pz
) can be demonstrated in shorter notation by using simplify() command on the command window in MATLAB.

Px = a2cosθ1cosθ2 + a4cosθ1cosθ4 cos(θ2 + θ3

) − a4cosθ1sinθ4 sin(θ2 + θ3

) +
a3cosθ1cos (θ2 + θ3)
- Px ⇒ cosθ1(a3 cos(θ2 + θ3
) + a2cosθ2 + a4cos(θ2 + θ3 + θ4

))

Py = a2cosθ2sinθ1 + a4cosθ4sinθ1 cos(θ2 + θ3

) − a4sinθ1sinθ4 sin(θ2 + θ3

) +
a3sinθ1cos (θ2 + θ3)
- Py ⇒ sinθ1(a3 cos(θ2 + θ3
) + a2cosθ2 + a4cos(θ2 + θ3 + θ4

))

Pz = d1 + a2sinθ2 + a4cosθ4sin (θ2 + θ3) + a4sinθ4cos (θ2 + θ3) + a3sin (θ2 + θ3)

- Pz ⇒ d1 + a3sin (θ2 + θ3) + a2sinθ2 + a4sin(θ2 + θ3 + θ4

)

Py
Px

=

sinθ1
cosθ1

= tanθ1 ⇒ θ1 = tan⁻¹ (

Py
Px

) or θ1 = Atan2(Py, Px)

If Px is multiplied by c1 and Py is multiplied by s1, A can be obtained explicitly.

Px. c1 + Py. s1 = a3 cos(θ2 + θ3

) + a2 cos θ2 + a4 cos(θ2 + θ3 + θ4

) = A

c23 =

(Px. c1 + Py. s1) − a2 cos θ2 + a4 cos(θ2 + θ3 + θ4 )
a3

And, also we obtained s23 by solving Pz

s23 =

Pz − d1 − a2sinθ2 − a2sin(θ2 + θ3 + θ4

)
a3

Substituting last two equations into the c23

2 + s23

2 = 1

((Px. c1 + Py. s1) − a2 cos θ2 + a4 cos(θ2 + θ3 + θ4

))

2
+ ( Pz − d1 − a2sinθ2 − a2sin(θ2 +

θ3 + θ4

))

2
= a3

2

((Px. c1 + Py. s1 + a4 cos(θ2 + θ3 + θ4

)) − a2 cos θ2))

2
+ ((Pz − d1 − a2sin(θ2 + θ3 +

θ4

)) − a2sinθ2)

2
= a3

2

(Px. c1 + Py. s1 + a4 cos(θ2 + θ3 + θ4

))

2
− 2(Px. c1 + Py. s1 + a4 cos(θ2 + θ3 + θ4

))a2 cos θ2) + a2

2
c2

2 + (Pz − d1 − a2sin(θ2 + θ3 + θ4 )

2 − 2(Pz − d1 − a2sin(θ2 + θ3 + θ4

)a2sinθ2 + a2

2
s2
2 | = a3
| 2

The equation can be regulated more comprehensible:

f = (Pz − d1 − a2sin(θ2 + θ3 + θ4

))

g = Px. c1 + Py. s1 + a4 cos(θ2 + θ3 + θ4

)

ℎ =

(Px. c1 + Py. s1 + a4 cos(θ2 + θ3 + θ4

) )

2
+ a2

2 + (Pz − d1 − a2sin(θ2 + θ3 + θ4 ))

2
− a3

2
2a2
- f sinθ2 + g cos θ2 = ℎ

(Px. c1 + Py. s1 + a4 cos(θ2 + θ3 + θ4

) ) cos θ2 + (Pz − d1 − a2sin(θ2 + θ3 + θ4

))sinθ2 =

⇒

(Px. c1 + Py. s1 + a4 cos(θ2 + θ3 + θ4

))

2
+ a2

2 + (Pz − d1 − a2sin(θ2 + θ3 + θ4 ))

2
− a3

2
2a2

= A

If the approximations are considered,

g + ℎ ≠ 0, | f√f
2 + g² − ℎ

2 − f

2 − g

2 − gℎ ≠ 0 → θ2

| ≈ 2.(3.14159n + tan⁻¹ (
f − √f
2 + g² − ℎ

2
f + g

)) , n ∈ Z

g + ℎ ≠ 0, | f√f
2 + g² − ℎ

2 + f

2 + g

2 + gℎ ≠ 0 → θ2

| ≈ 2.(3.14159n + tan⁻¹ (
f + √f
2 + g² − ℎ

2
f + g

)) , n ∈ Z

f ≠ 0 , f

2 + g

2 ≠ 0, ℎ ≈ −f → θ2 ≈ 2. (3.14159n + tan⁻¹ ( g
f

)) , n ∈ Z

g = −f → θ2 = 2πn + π, n ∈ Z

And if g = −f , x = 2πn + π it is possible to obtain as follows:

θ2 = Atan2 (
gℎ − √f
4 + f

2g² − f

2ℎ

2
f

2 + g²

,

1
f

(
g√−f
2(−f

2 − g² + ℎ

2) − g

2ℎ
f
2 + g² | + ℎ))

θ2 = Atan2 (
gℎ + √f
4 + f

2g² − f

2ℎ

2
f

2 + g²

,

1
f

(
−g√−f
2(−f

2 − g² + ℎ

2) − g

2ℎ
f
2 + g² | + ℎ))

If we consider c23 and s23 from the previous equations to obtain tan(θ2 + θ3)

tan(θ2 + θ3

) =

Pz − d1 − a2sinθ2 − a2sin(θ2 + θ3 + θ4

)
(Px. c1 + Py. s1) − a2 cos θ2 + a4 cos(θ2 + θ3 + θ4 )

Now, θ3 can be obtained easily.

θ3 = Atan2(Pz − d1 − a2sinθ2 − a2sin(θ2 + θ3 + θ4

), (Px. c1 + Py. s1)
− a2 cos θ2 + a4 cos(θ2 + θ3 + θ4

)) − θ2

Py4
3
Px4
3

=

s4
c4

= θ4 = Atan2(Py4
3, Px4

3 ) = θ234 − θ2 − θ3

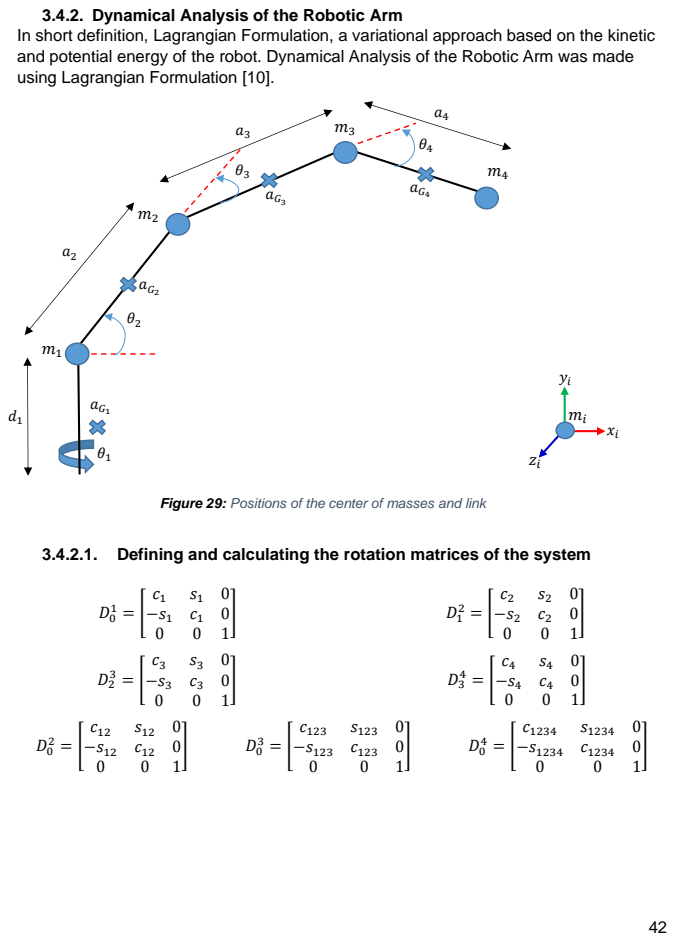
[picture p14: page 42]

3.4.2. Dynamical Analysis of the Robotic Arm
In short definition, Lagrangian Formulation, a variational approach based on the kinetic
and potential energy of the robot. Dynamical Analysis of the Robotic Arm was made
using Lagrangian Formulation [10].

Figure 29: Positions of the center of masses and link

3.4.2.1. Defining and calculating the rotation matrices of the system

### 3.4.2.2. Defining the angular velocities of the sequential links

ω0

0
(R0

) = [

0
0
0

] ω1
0
(R0

) = [

0
0
θ̇
1

] ω2
0
(R1

) = [

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
) = [

0
0
θ̇
3

] ω4
0
(R3

) = [

0
0
θ̇
4

]

### 3.4.2.3. Calculating the angular velocities of the overall links

ω1

0
(R1

) = ω1

0
(R0

) + D0

1 ω0

0
(R0

) = [

0
0
θ̇
1

] + [

c1 | s1 | 0
−s1 | c1 | 0
0 | 0 1

][

0
0/0] = [

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
) = ω2

1
(R1

) + D1

2 ω1

0
(R1

) = [

0
0
θ̇
2

] + [

c2 | s2 | 0
−s2 | c2 | 0
0 | 0 1

][

0
0
θ̇
1

] = [

0
0
θ̇

1 + θ̇
2

]

ω3

0
(R3

) = ω3

2
(R2

) + D2

3 ω2

0
(R2

) = [

0
0
θ̇
3

] + [

c3 | s3 | 0
−s3 | c3 | 0
0 | 0 1

][

0
0
θ̇

1 + θ̇
2

] = [

0
0
θ̇

1 + θ̇

2 + θ̇
3

]

ω4

0
(R4

) = ω4

3
(R3

) + D3

4 ω3

0
(R3

) = [

0
0
θ̇
4

] + [

c4 | s4 | 0
−s4 | c4 | 0
0 | 0 1

][

0
0
θ̇

1 + θ̇

2 + θ̇
3

]

= [

0
0
θ̇

1 + θ̇

2 + θ̇

3 + θ̇
4

]

There are 2 types of the kinetic energy of the system and one of them is translational kinetic energy and the other is rotational kinetic energy.

### 3.4.2.4. Calculating of the Rotational Kinetic Energy

KE1

(R) =

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
)] =

1
2

[0 0 θ̇
1

]. [
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
] .[
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
(R) =

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
)] =

1
2

[0 0 θ̇

1 + θ̇
2

]. [
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
] .[
0
0
θ̇

1 + θ̇
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
1+θ̇
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
(R) =

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
)] =

1
2

[0 0 θ̇

1 + θ̇

2 + θ̇
3

]. [
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
] .[
0
0
θ̇

1 + θ̇

2 + θ̇
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
1+θ̇

2+θ̇
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
2) +

1
2

Izz

3

(θ̇

1θ̇
3) +

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
(R) =

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
)] =

1
2

[0 0 θ̇

1 + θ̇

2 + θ̇

3 + θ̇
4

]. [
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
] .[
0
0
θ̇

1 + θ̇

2 + θ̇

3 + θ̇
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
1+θ̇

2+θ̇

3+θ̇
4)

2

which Izz

n
is equal to the moment of inertia of n

tℎ
link. The spoon, it means manipulator, is 4

tℎ
link on the system.

### 3.4.2.5. Calculating the linear velocity vectors of the center of masses

vG0

0
(R0

) = 0

vG1

0
(R1

) = v1

0
(R1

) + vG1

1
(R1

) + ω1

0
(R1

)xO1G1

(R1

) = [

0
0/0] + [

0
0/0] + [

0
0
θ̇
1

] x [

aG1
0/0] = [

0
aG1

θ̇
1
0

]

which is the meaning of aG1

is the length from G1 to O1 on the second link that its length is a2.

v2

0
(R1

) = v1

0
(R1

) + v2

1
(R1

) + ω1

0
(R1

)xO1O2

(R1

) = [

0
0/0] + [

0
0/0] + [

0
0
θ̇
1

] x [

a2
0/0] = [

0
a2θ̇
1
0

]

which is the definition of a2 is the length of the second link.

v2

0
(R2

) = D1

2 v2

0
(R1

) = [

c2 | s2 | 0
−s2 | c2 | 0
0 | 0 1

][

0
a2θ̇
1
0

] = [

a2θ̇
1s2
a2θ̇
1c2
0

]

vG2

0
(R2

) = v2

0
(R2

) + vG2

2
(R2

) + ω2

0
(R2

)xO2G2

(R2

) = [

a2θ̇
1s2
a2θ̇
1c2
0

] + [

0
0/0] + [

0
0
θ̇

1 + θ̇
2

] x [

aG2
0/0] =

= [

a2θ̇
1s2
aG2

(θ̇

1 + θ̇
2) + a2θ̇
1c2
0

]

which is the meaning of aG2

is the length from G2 to O2 on the third link that its length is a3.

v3

0
(R2

) = v2

0
(R2

) + v3

2
(R2

) + ω2

0
(R2

)xO2O3

(R2

) = [

a2θ̇
1s2
a2θ̇
1c2
0

] + [

0
0/0] + [

0
0
θ̇

1 + θ̇
2

] x [

a3
0/0] =

= [
a2θ̇
1s2
a3(θ̇

1 + θ̇
2) + a2θ̇
1c2
0

]

which is the definition of a3 is the length of the third link.

v3

0
(R3

) = D2

3 v3

0
(R2

) = [

c3 | s3 | 0
−s3 | c3 | 0
0 | 0 1

]. [
a2θ̇
1s2
a3(θ̇

1 + θ̇
2) + a2θ̇
1c2
0

]

= [

(a2s23 + a3s3

)θ̇

1 + a3s3θ̇
2
(a2c23 + a3c3

)θ̇

1 + a3c3θ̇
2
0

]

vG3

0
(R3

) = v3

0
(R3

) + vG3

3
(R3

) + ω3

0
(R3

)xO3G3

(R3

) =

= [
(a2s23 + a3s3

)θ̇

1 + a3s3θ̇
2
(a2c23 + a3c3

)θ̇

1 + a3c3θ̇
2
0

] + [
0
0/0] + [

0
0
θ̇

1 + θ̇

2+θ̇
3

] x [

aG3
0/0]

= [

(a3s3 + a2s23)θ̇

1 + a3s3θ̇
2
(aG3 + a3c3 + a2c23)θ̇

1 + (aG3 + a3c3)θ̇
2 + aG3

θ̇
3
0

]

v4

0
(R3

) = v3

0
(R3

) + v4

3
(R3

) + ω3

0
(R3

)xO3O4

(R3

) =

= [

(a3s3 + a2s23)θ̇

1 + a3s3θ̇
2
(aG3 + a3c3 + a2c23)θ̇

1 + (aG3 + a3c3)θ̇
2 + aG3

θ̇
3
0

] + [
0
0/0] + [

0
0
θ̇

1 + θ̇

2 + θ̇
3

] x [

a4
0/0]

= [

(a3s3 + a2s23)θ̇

1 + a3s3θ̇
2
(aG3 + a4 + a3c3 + a2c23)θ̇

1 + (aG3 + a4 + a3c3)θ̇

2 + (aG3 + a4)θ̇
3
0

]

v4

0
(R4

) = D3

4 v4

0
(R3

) =
= [
c4 | s4 | 0
−s4 | c4 | 0
0 | 0 1

] [

(a3s3 + a2s23)θ̇

1 + a3s3θ̇
2
(aG3 + a4 + a3c3 + a2c23)θ̇

1 + (aG3 + a4 + a3c3)θ̇

2 + (aG3 + a4)θ̇
3
0

]

= [

((aG3 + a4 + a3c3 + a2c23)s4 + (a3s3 + a2s23)c4) θ̇ 1 + (s4(aG3 + a4 + a3c3) + a3s3c4)θ̇

2 + (aG3 + a4)s4θ̇
3
((aG3 + a4 + a3c3 + a2c23)c4 − (a3s3 + a2s23)s4) θ̇ 1 + (c4(aG3 + a4 + a3c3) − a3s3s4)θ̇

2 + (aG3 + a4)c4θ̇
3
0

]

vG4

0
(R4

) = v4

0
(R4

) + vG4

4
(R4

) + ω4

0
(R4

)xO4G4

(R4

) =

= [

((aG3 + a4 + a3c3 + a2c23)s4 + (a3s3 + a2s23)c4) θ̇ 1 + (s4(aG3 + a4 + a3c3) + a3s3c4)θ̇

2 + (aG3 + a4)s4θ̇
3
((aG3 + a4 + a3c3 + a2c23)c4 − (a3s3 + a2s23)s4) θ̇ 1 + (c4(aG3 + a4 + a3c3) − a3s3s4)θ̇

2 + (aG3 + a4)c4θ̇
3
0

]

+ [

0
0/0] + [

0
0
θ̇

1 + θ̇

2 + θ̇

3 + θ̇
4

] x [

a4
0/0]

### 3.4.2.6. Calculating the translational kinetic energies of the system

KE1

(T) =

1
2

m1[VG1

0
(R1

)]

T
[VG1

0
(R1

)] =

1
2

m1[0 aG1

θ̇

1 0][

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
m1(aG1
θ̇

1)

2

KE2

(T) =

1
2

m2[VG2

0
(R2)]

T
[VG2

0
(R2)] =

1
2

m2[a2s2θ̇

1 (aG2 + a2c2)θ̇
1 + aG2

θ̇

2 0] [

a2s2θ̇
1
(aG2 + a2c2)θ̇
1 + aG2

θ̇
2
0

]

⇒ (

1
2

m2(a2

2 + aG2

2
) + m2aG2

a2c2) (θ̇
1)

2
+

1
2

m2aG2

2

(θ̇
2)

2
+ m2(aG2 + a2c2)aG2

θ̇

1θ̇
2

KE3

(T) =

1
2

m3 [VG3

0
(R3)]

T
[VG3

0
(R3)] ⇒

=

1
2

m3 (a2
2 + a3

2 + 2a3a2c2 + 2aG3

(a3c3 + a2c23)) (θ̇
1)

2
+

1
2

m3(a3

2 + aG3

2 +

2aG3

a3c3)(θ̇
2)

2
+ m3aG3

2

(θ̇
3)

2
+

1
2

m3 (a3
2
s3

2 + a2a3s3s23 + 2(aG3

2 + 2aG3
a3c3 + a3

2
c3

2 +

aG3

a2c23 + a2a3c3c23)) θ̇
1θ̇
2 + m3(aG3

2 + aG3
a3c3 + aG3

a2c23)θ̇

1θ̇

3 + m3(aG3 + a3c3)θ̇

2θ̇
3

=

1
2

m3

[(a3s3 + a2s23)θ̇

1 + a3s3θ̇

2 (aG3 + a3c3 + a2c23)θ̇

1 + (aG3 + a3c3)θ̇
2 + aG3

θ̇

3 0] [

(a3s3 + a2s23)θ̇

1 + a3s3θ̇
2
(aG3 + a3c3 + a2c23)θ̇

1 + (aG3 + a3c3)θ̇
2 + aG3

θ̇
3
0

]

= [

((aG3 + a4 + a3c3 + a2c23)s4 + (a3s3 +a2s23)c4) θ̇ 1 + (s4(aG3 + a4 + a3c3) + a3s3c4)θ̇

2 + (aG3 +a4)s4θ̇
3
((aG3 + a4 + a3c3 + a2c23)c4 − (a3s3 + a2s23)s4 + a4) θ̇ 1 + (c4(aG3 + a4 +a3c3) −a3s3s4 + a4)θ̇

2 +(c4(aG3 + a4) + a4)θ̇

3 + a4θ̇
4
0

]

KE4

(T) =

1
2

m4 [VG4

0
(R4)]

T
[VG4

0
(R4)] =

1
2

m4(2a4 + aG3 + a2c23 + a3c3 + a4c4 + aG3 c4 +
a2c23c4 + a3c3c4 − a2s23s4 − a3s3s4 − a2s23c4 − a3s3c4)(θ̇
1)

2
+

1
2

m4(a4c4 + aG3
c4 +

a3c3c4 − a3s3s4 − a3s3c4 + a4s4 + aG3

s4 + a3c3s4 + a4)(θ̇
2)

2
+

1
2

m4(a4c4 + aG3
c4 + a4 +
aG3 + a4)(θ̇
3)

2
+

1
2

m4a4(θ̇
4)

2
+ 2θ̇

1θ̇

2 + 2θ̇

1θ̇

3 + 2θ̇

1θ̇

4 + 2θ̇

2θ̇

3 + 2θ̇

2θ̇

4 + 2θ̇

3θ̇
4

From the calculated kinetic energies, the total kinetic will be as the following;

KE = KE

(R) + KE

(T)

⇒

1
2

{Izz
1 + Izz

2 + Izz

3 + Izz

### 4 + m1aG1

2 + m2(a2
2 + aG2

2 + 2aG2

### a2c2) + m3 (a2

2 +

a3

### 2 + 2a3a2c2 + 2aG3

### (a3c3 + a2c23)) + m4(a4 + aG3 + a2c23 + a3c3 + a4c4 +

aG3

### c4 + a2c23c4 + a3c3c4 − a2s23s4 − a3s3s4 − a2s23c4 − a3s3c4 +

a4)} (θ̇
1)

2
+

1
2

{Izz

2 + Izz

3 + Izz

### 4 + m2aG2

2 + m3(a3
2 + aG3

2 + 2aG3
a3c3) +

### m4(a4c4 + aG3 c4 + a3c3c4 − a3s3s4 − a3s3c4 + a4s4 + aG3

### s4 + a3c3s4 +

a4)}(θ̇
2)

2
+

1
2

{Izz

3 + Izz

### 4 + 2m3aG3

### 2 + m4(a4c4 + aG3 c4 + a4 + aG3 +

a4)}(θ̇
3)

2
+

1
2

{Izz

4 + m4a4

}(θ̇
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
### 4 + m2(aG2

### 2 + a2c2aG2

) +

1
2

m3 (a3
2
s3

### 2 + a2a3s3s23 + 2(aG3

2 + 2aG3

### a3c3 + a3

2
c3

2 + aG3
a2c23 +

### a2a3c3c23)) + 2} θ̇

1θ̇

2 + {

1
2

Izz

3 +

1
2

Izz

### 4 + m3(aG3

2 + aG3

### a3c3 + aG3

a2c23) +
2} θ̇
1θ̇

3 + {

1
2

Izz

3 +

1
2

Izz

### 4 + m3(aG3 + a3c3) + 2} θ̇

2θ̇
3 + {Izz

4 + 2}θ̇

1θ̇
4 +

{Izz

4 + 2}θ̇

2θ̇
4 + {Izz

4 + 2}θ̇

3θ̇
4

Now, some parameters must be defined to take derivatives easily.

k1 = Izz

1 + Izz

2 + Izz

3 + Izz

4 + m1aG1

2 + m2a2
2 + m2aG2

2

k2 = 2m2aG2

a2

k3 = m3

(a2

2 + a3

2
)

k4 = 2m3a3a2

k5 = 2m3aG3

a3

k6 = 2m3aG3

a2

k7 = m4(2a4 + aG3

)

k8 = m4a2

k9 = m4a3

k10 = m4a4

k11 = m4aG3

k12 = Izz

2 + Izz

3 + Izz

4 + m2aG2

2 + m3(a3
2 + aG3

2
)

k13 = m4a4

k14 = Izz

3 + Izz

4 + 2m3aG3

2 + m4(2a4 + aG3
)

k15 = Izz

4 + m4a4

k16 =

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
4 + m2aG2

2

k17 = m3aG3

2

k18 = m3a3

2

k19 =

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
k20 = m3aG3

k21 = m3a3

k22 = Izz

4 + 2

The total kinetic energy can be defined as the following:

KE =

1
2

(k1 + k2c2 + k3 + k4c2 + k5c3 + k6c23+k7 + k8c23 + k9c3 + k10c4 +

k11c4+k8c23c4 + k9c3c4 − k8s23s4 − k9s3s4 − k8s23c4 − k9s3c4

)(θ̇
1)

2
+

1
2

(k12 + k5c3 +

k13 + k13c4 + k11c4 + k9c3c4 − k9s3s4 − k9s3c4 + k10s4 + k11s4 + k9c3s4

)(θ̇
2)

2
+

1
2

(k14 + k10c4 + k11c4

)(θ̇
3)

2
+

1
2

k15(θ̇
4)

2
+ (k16 +

k2
2

c2 +

k18
2

s3

2 +

k4
2

s3s23 + k17 + k5 +

k18c3

2 +

k6
2

c23 +

k4
2

c3c23 + 2) θ̇
1θ̇

2 + (k19 + k17 +

k5
2

c3 +

k6
2

c23 + 2) θ̇
1θ̇
3 +
(k19 + k20 + k21c3 + 2)θ̇

2θ̇

3 + k22θ̇

1θ̇

4 + k22θ̇

2θ̇

4 + k22θ̇

3θ̇
4

### 3.4.2.7. Calculating the potential energies of the system

P1 = m1. g. y1 = m1. g. d1

P2 = m2. g. y2 = m2. g. (d1 + a2sinθ2)

P3 = m3. g. y3 = m3. g. (d1 + a2sinθ2 + a3sinθ3)

P4 = m4. g. y4 = m4. g. (d1 + a2sinθ2 + a3sinθ3 + a4sinθ4)

PE = P1 + P2 + P3 + P4

⇒ (m1 + m2 + m3 + m4

)g. d1 + (m2 + m3 + m4

)ga2sinθ2 + (m3 + m4

)ga3sinθ3
+ m4. ga4sinθ4

which is PE is equal to the total potential energy of the system.

### 3.4.2.8. Calculating of Lagrangian Function

ℒ(θ, θ̇) = ∑(Ki − Pi)

4

i=1

and τi =

d

dt (
∂ℒ
∂θ̇
i

) −
∂ℒ
∂θi

i = 1,2,3,4

In order to determine the Euler-Lagrange equations in a specific situation, one has to form the Lagrangian of the system which is the difference between the kinetic energy and potential energy.

ℒ(θ, θ̇) = ∑(Ki − Pi)

4

i=1

= (K1 + K2 + K3 + K4

) − (P1 − P2 − P3 − P4

) = KE−PE

⇒

1
2

(k1 + k2c2 + k3 + k4c2 + k5c3 + k6c23+k7 + k8c23 + k9c3 + k10c4 + k11c4+k8c23c4 +

k9c3c4 − k8s23s4 − k9s3s4 − k8s23c4 − k9s3c4

)(θ̇
1)

2
+

1
2

(k12 + k5c3 + k13 + k13c4 +

k11c4 + k9c3c4 − k9s3s4 − k9s3c4 + k10s4 + k11s4 + k9c3s4

)(θ̇
2)

2
+

1
2

(k14 + k10c4 +

k11c4

)(θ̇
3)

2
+

1
2

k15(θ̇
4)

2
+ (k16 +

k2
2

c2 +

k4
2

s3s23 + k17 + k5 + k18 +

k6
2

c23 +

k4
2

c3c23 +
2) θ̇
1θ̇

2 + (k19 + k17 +

k5
2

c3 +

k6
2

c23 + 2) θ̇
1θ̇

3 + (k19 + k20 + k21c3 + 2)θ̇

2θ̇

3 + k22θ̇

1θ̇
4 +
k22θ̇

2θ̇

4 + k22θ̇

3θ̇
4 − (m1 + m2 + m3 + m4

)g. d1 − (m2 + m3 + m4

)ga2sinθ2 −
(m3 + m4

)ga3sinθ3 − m4. ga4sinθ4

### 3.4.2.9. Calculating the Partial Derivatives of the Lagrangian Function

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
### (k4 + k6s23 + k8s23+k8s23c4 + k8c23s4 + k8c23c4

)(θ̇
1)

2
− (

k2
2

s2 −

k4
2

s3c23 +

k6
2

s23 +

k4
2

### c3s23) θ̇

1θ̇
2 −

k6
2

s23θ̇

1θ̇

### 3 + (m2 + m3 + m4

### )ga2c2

∂ℒ
∂θ3

= −

1
2

### (k5s3 + k6s23 + k8s23 + k9s3+k8s23c4 + k9s3c4 + k8c23s4 +

### k9c3s4 + k8c23c4 + k9c3c4

)(θ̇
1)

2
−

1
2

### (k5s3 + k9s3c4 + k9c3s4 +

### k9c3c4

)(θ̇
2)

2
+ (

k4
2

s3c23 −

k6
2

s23 +

k4
2

s2) θ̇
1θ̇

2 − (

k5
2

s3 +

k6
2

s23) θ̇
1θ̇
3 −

### k21s3θ̇

2θ̇
3 − (m3 + m4

### )ga3c3

∂ℒ
∂θ4

= −

1
2

### (k10s4 + k11s4+k8c23s4 − k9c3s4 + k8s23c4 − k9s3c4 + k8s23s4 +

### k9s3s4

)(θ̇
1)

2
+

1
2

### (−k13c4 − k11c4 − k9c3c4 − k9s3c4 + k9s3s4 + k10c4 +

### k11c4 + k9c3c4

)(θ̇
2)

2
−

1
2

### (k10s4 + k11s4

)(θ̇
3)

2

### −m4. ga4c4

∂ℒ
∂θ̇
1

### = (k1 + k2c2 + k3 + k4c2 + k5c3 + k6c23+k7 + k8c23 + k9c3 + k10c4 +

### k11c4+k8c23c4 + k9c3c4 − k8s23s4 − k9s3s4 − k8s23c4 − k9s3c4

)θ̇

1 + (k16 +

k2
2

c2 + k18 +

k4
2

### s3s23 + k17 + k5 +

k6
2

c23 +

k4
2

### c3c23 + 2) θ̇

2 + (k19 + k17 +

k5
2

c3 +

k6
2

c23 + 2) θ̇
3

∂ℒ
∂θ̇
2

= (k16 +

k2
2

c2 + k18 +

k4
2

### s3s23 + k17 + k5 +

k6
2

c23 +

k4
2

### c3c23 + 2) θ̇

1 +

### (k12 + k5c3 + k13 + k13c4 + k11c4 + k9c3c4 − k9s3s4 − k9s3c4 + k10s4 + k11s4 + k9c3s4

)θ̇

### 2 + (k19 + k20 + k21c3 + 2)θ̇

3 + k22θ̇
4

∂ℒ
∂θ̇
3

= (k19 + k17 +

k5
2

c3 +

k6
2

c23 + 2) θ̇

### 1 + (k19 + k20 + k21c3 + 2)θ̇

2 + (k14 +

### k10c4 + k11c4

)θ̇

3 + k22θ̇
4

∂ℒ
∂θ̇
4

= k22θ̇

1 + k22θ̇

2 + k22θ̇

3 + k15θ̇
4

d
dt (

∂ℒ
∂θ̇
1

### ) = (k1 + k2c2 + k3 + k4c2 + k5c3 + k6c23+k7 + k8c23 + k9c3 +

### k10c4 + k11c4+k8c23c4 + k9c3c4 − k8s23s4 − k9s3s4 − k8s23c4 − k9s3c4

)θ̈
1 +
(k16 +

k2
2

c2 + k18 +

k4
2

### s3s23 + k17 + k5 +

k6
2

c23 +

k4
2

### c3c23 + 2) θ̈

2 + (k19 +

k17 +

k5
2

c3 +

k6
2

c23 + 2) θ̈

### 3 + (−k2s2 − k4s2 − k6s23 − k8s23 − k8s23c4 −

### k8s23s4 − k8c23c4

)(θ̇

1θ̇

### 2) + (−k5s3 − k6s23 − k8s23 − k8s23c4 − k9s3c4 − k8c23s4 − k9c3s4 − k8c23c4

)(θ̇

1θ̇

### 3) + (−k10s4 − k11s4 − k8c23s4 − k9c3s4 −

### k8s23c4 − k9s3c4 + k8s23s4 + k9s3s4

)(θ̇

1θ̇

4) + (−

k2
2

s2 +

k4
2

s3c23 −

k6
2

s23 −

k4
2

### c3s23) θ̇

2

2 + (

k4
2

### s3c23 − k6s23 −

k4
2

s3c23 −

k4
2

### c3s23) (θ̇

2θ̇

3) + (−

k5
2

s3 −

k6
2

s23) θ̇
3

2

d
dt (

∂ℒ
∂θ̇
2

) = (k16 +

k2
2

c2 + k18 +

k4
2

### s3s23 + k17 + k5 +

k6
2

c23 +

k4
2

### c3c23 + 2) θ̈

1 +

### (k12 + k5c3 + k13 + k13c4 + k11c4 + k9c3c4 − k9s3s4 − k9s3c4 + k10s4 +

### k11s4 + k9c3s4

)θ̈

### 2 + (k19 + k20 + k21c3 + 2)θ̈

3 + k22θ̈

4 + (−

k2
2

s2 +

k4
2

s3c23 −

k6
2

s23 −

k4
2

### c3s23) (θ̇

1θ̇

2) + (

k4
2

c3s23 −

k6
2

s23) (θ̇
1θ̇

### 3) + (−k5s3 − k9s3c4 −

### k9c3s4 − k9s3s4

)(θ̇

2θ̇

### 3) + (−k13s4 − k11s4 − k9c3s4 − k9s3c4 + k9c3c4 + k10c4 + k11c4

)(θ̇

2θ̇

### 4) − k21s3θ̇

3

2

d
dt (

∂ℒ
∂θ̇
3

) = (k19 + k17 +

k5
2

c3 +

k6
2

c23 + 2) θ̈

### 1 + (k19 + k20 + k21c3 + 2)θ̈

2 +

### (k14 + k10c4 + k11c4

)θ̈

3 + k22θ̈
4 −

k6
2

s23(θ̇

1θ̇

2) + (−

k5
2

s3 −

k6
2

s23) (θ̇
1θ̇
3) −

### k21s3(θ̇

2θ̇

### 3) + (−k10s4 + k11s4

)(θ̇

3θ̇
4)

d

dt (
∂ℒ
∂θ̇
4

) = k22θ̈
1 + k22θ̈

2 + k22θ̈

3 + k15θ̈
4

### 3.4.2.10. Calculating the Torque Values of all joints

τi =

d

dt (
∂ℒ
∂θ̇
i

) −
∂ℒ
∂θi

i = 1,2,3,4

### τ1 = (k1 + k2c2 + k3 + k4c2 + k5c3 + k6c23+k7 + k8c23 + k9c3 + k10c4 + k11c4+k8c23c4 + k9c3c4 − k8s23s4 − k9s3s4 − k8s23c4 − k9s3c4

)θ̈
1 +
(k16 +

k2
2

c2 + k18 +

k4
2

### s3s23 + k17 + k5 +

k6
2

c23 +

k4
2

### c3c23 + 2) θ̈

2 +
(k19 + k17 +

k5
2

c3 +

k6
2

c23 + 2) θ̈

### 3 + (−k2s2 − k4s2 − k6s23 − k8s23 −

### k8s23c4 − k8s23s4 − k8c23c4

)(θ̇

1θ̇

### 2) + (−k5s3 − k6s23 − k8s23 − k8s23c4 − k9s3c4 − k8c23s4 − k9c3s4 − k8c23c4

)(θ̇

1θ̇

### 3) + (−k10s4 − k11s4 − k8c23s4 −

### k9c3s4 − k8s23c4 − k9s3c4 + k8s23s4 + k9s3s4

)(θ̇

1θ̇

4) + (−

k2
2

s2 +

k4
2

s3c23 −

k6
2

s23 −

k4
2

### c3s23) θ̇

2

2 + (

k4
2

### s3c23 − k6s23 −

k4
2

s3c23 −

k4
2

### c3s23) (θ̇

2θ̇
3) +
(−

k5
2

s3 −

k6
2

s23) θ̇
3

2

τ2 = (k16 +

k2
2

c2 + k18 +

k4
2

### s3s23 + k17 + k5 +

k6
2

c23 +

k4
2

### c3c23 + 2) θ̈

1 +

### (k12 + k5c3 + k13 + k13c4 + k11c4 + k9c3c4 − k9s3s4 − k9s3c4 + k10s4 +

### k11s4 + k9c3s4

)θ̈

### 2 + (k19 + k20 + k21c3 + 2)θ̈

3 + k22θ̈

4 + (−

k2
2

s2 +

k4
2

s3c23 −

k6
2

s23 −

k4
2

### c3s23) (θ̇

1θ̇

2) + (

k4
2

c3s23 −

k6
2

s23) (θ̇
1θ̇

### 3) + (−k5s3 − k9s3c4 −

### k9c3s4 − k9s3s4

)(θ̇

2θ̇

### 3) + (−k13s4 − k11s4 − k9c3s4 − k9s3c4 + k9c3c4 +

### k10c4 + k11c4

)(θ̇

2θ̇

### 4) − k21s3θ̇

3

2 −

1
2

### (k4 + k6s23 + k8s23+k8s23c4 + k8c23s4 +

### k8c23c4

)(θ̇
1)

2
− (

k2
2

s2 −

k4
2

s3c23 +

k6
2

s23 +

k4
2

### c3s23) θ̇

1θ̇
2 −

k6
2

s23θ̇

1θ̇
3 +

### (m2 + m3 + m4

### )ga2c2

### τ3 = (k19 + k17 +

k5
2

c3 +

k6
2

c23 + 2) θ̈

### 1 + (k19 + k20 + k21c3 + 2)θ̈

2 +

### (k14 + k10c4 + k11c4

)θ̈

3 + k22θ̈
4 −

k6
2

s23(θ̇

1θ̇

2) + (−

k5
2

s3 −

k6
2

s23) (θ̇
1θ̇
3) −

### k21s3(θ̇

2θ̇

### 3) + (−k10s4 + k11s4

)(θ̇

3θ̇
4) −

1
2

### (k5s3 + k6s23 + k8s23 +

### k9s3+k8s23c4 + k9s3c4 + k8c23s4 + k9c3s4 + k8c23c4 + k9c3c4

)(θ̇
1)

2
−

1
2

### (k5s3 + k9s3c4 + k9c3s4 + k9c3c4

)(θ̇
2)

2
+ (

k4
2

s3c23 −

k6
2

s23 +

k4
2

s2) θ̇
1θ̇
2 −
(

k5
2

s3 +

k6
2

s23) θ̇
1θ̇

### 3 − k21s3θ̇

2θ̇
3 + (m3 + m4

### )ga3c3

### τ4 = k22θ̈

1 + k22θ̈

2 + k22θ̈

3 + k15θ̈
4 −

1
2

### (k10s4 + k11s4+k8c23s4 − k9c3s4 +

### k8s23c4 − k9s3c4 + k8s23s4 + k9s3s4

)(θ̇
1)

2
+

1
2

### (−k13c4 − k11c4 − k9c3c4 −

### k9s3c4 + k9s3s4 + k10c4 + k11c4 + k9c3c4

)(θ̇
2)

2
−

1
2

(k10s4 +

k11s4

)(θ̇
3)

2

### +m4. ga4c4

### 3.4.2.11. Finding Mass Matrix, C Vector and Gravity Vector

τ = M(θ)θ̈+ c(θ, θ̇) + g(θ)

- M(θ) = [
n11 | n12 | n13 | n14
n21 | n22 | n23 | n24
n31 | n32 | n33 | n34
n41 | n42 | n43 | n44

]

### n11 = k1 + k2c2 + k3 + k4c2 + k5c3 + k6c23+k7 + k8c23 + k9c3 + k10c4 + k11c4+k8c23c4 + k9c3c4 − k8s23s4 − k9s3s4 − k8s23c4 − k9s3c4

n12 = k16 +

k2
2

c2 + k18 +

k4
2

### s3s23 + k17 + k5 +

k6
2

c23 +

k4
2

c3c23 + 2

### n13 = k19 + k17 +

k5
2

c3 +

k6
2

c23 + 2

n14 = 0

n21 = k16 +

k2
2

c2 + k18 +

k4
2

### s3s23 + k17 + k5 +

k6
2

c23 +

k4
2

c3c23 + 2

### n22 = k12 + k5c3 + k13 + k13c4 + k11c4 + k9c3c4 − k9s3s4 − k9s3c4 + k10s4 + k11s4 + k9c3s4

### n23 = k19 + k20 + k21c3 + 2

n24 = k22

### n31 = k19 + k17 +

k5
2

c3 +

k6
2

c23 + 2

### n32 = k19 + k20 + k21c3 + 2

### n33 = k14 + k10c4 + k11c4

n34 = k22

n41 = k22

n42 = k22

n43 = k22

n44 = k22

- c(θ, θ̇) = [
p11 | p12 | p13 | p14
p21 | p22 | p23 | p24
p31 | p32 | p33 | p34
p41 | p42 | p43 | p44

]

### p11 = (−k2s2 − k4s2 − k6s23 − k8s23 − k8s23c4 − k8s23s4 − k8c23c4

)(θ̇
2) +

### (−k5s3 − k6s23 − k8s23 − k8s23c4 − k9s3c4 − k8c23s4 − k9c3s4 − k8c23c4

)(θ̇

### 3) + (−k10s4 − k11s4 − k8c23s4 − k9c3s4 − k8s23c4 − k9s3c4 + k8s23s4 + k9s3s4

)(θ̇
4)

p12 = (−

k2
2

s2 +

k4
2

s3c23 −

k6
2

s23 −

k4
2

### c3s23) θ̇

2 + (

k4
2

### s3c23 − k6s23 −

k4
2

s3c23 −

k4
2

### c3s23) (θ̇

3)

p13 = (−

k5
2

s3 −

k6
2

s23) θ̇
3

p14 = 0

p21 = −

1
2

### (k4 + k6s23 + k8s23+k8s23c4 + k8c23s4 + k8c23c4

)(θ̇
1) +

### (−k2s2 + k4s3c23 − k6s23 − k4c3s23)(θ̇

2) + (

k4
2

### c3s23 − k6s23) (θ̇

3)

### p22 = (−k5s3 − k9s3c4 − k9c3s4 − k9s3s4

)(θ̇

### 3) + (−k13s4 − k11s4 − k9c3s4 − k9s3c4 + k9c3c4 + k10c4 + k11c4

)(θ̇
4)

### p23 = −k21s3θ̇

3
p24 = 0

p31 = (

k6
2

s23 +

k4
2

s3c23 −

k6
2

s23 +

k4
2

s2) (θ̇

### 2) + (−k5s3 − k6s23)(θ̇

3)

p32 = −

1
2

### (k5s3 + k9s3c4 + k9c3s4 + k9c3c4

)(θ̇

### 2) − k21s3θ̇

### 3 − k21s3θ̇

3

### p33 = (−k10s4 + k11s4

)(θ̇
4)

p34 = 0

p41 = −

1
2

### (k10s4 + k11s4+k8c23s4 − k9c3s4 + k8s23c4 − k9s3c4 + k8s23s4 + k9s3s4

)(θ̇
1)

p42 =

1
2

### (−k13c4 − k11c4 − k9c3c4 − k9s3c4 + k9s3s4 + k10c4 + k11c4 + k9c3c4

)(θ̇
2)

p43 = −

1
2

### (k10s4 + k11s4

)(θ̇
3)

p44 = 0

g(θ) = [

0
(m2 + m3 + m4

)ga2cosθ2 + (m3 + m4

)ga3cos(θ2 + θ3

) + m4ga4cos(θ2 + θ3 + θ4

)
(m3 + m4

)ga3cos(θ2 + θ3

) + m4ga4cos(θ2 + θ3 + θ4

)
m4ga4cos(θ2 + θ3 + θ4

)

]

### 3.5. Image Processing

The food taken from the plate as a result of eye-tracking is brought to the pre-fixed position and the mouth tracking algorithm is started.

In the case of mouth scanning, the frame is taken from the camera 30 frames per second for each second which corresponds to 30 fps. Then, these frames are gray filtered and the image is grayed out to perform facial detection with ‘frontal face.xml’ which is one of the open-source HaarCascade classifiers [11]. After filtering, the Frontal Face HaarCascade algorithm was applied and face detection was performed.

After the face is found, a new pixel set is defined to process the pixels on which the face is found. HaarCascade classifiers are used again to find the mouth in the resulting cluster and this time ‘mcs_mouth.xml ‘
is used [12].

The basis of the HaarCascade classifier is that artificial intelligence trains the given data and learn what the mouth looks like. Images taken from datasets are divided into two, positive and negative images. While positive images contain the object we are looking for, negative images should not contain or even resemble this object. In general, the number of negative images is greater than the number of positive images. It should be noted that the more data, the better the HaarCascade classifier works. The tiring part is the selection of individual objects from positive images. Software is available on the Internet to simplify this process but still takes time. After the selection of the objects is finished, these data are trained with artificial intelligence and the HaarCascade algorithm is created. Even if the open-source HaarCascade classifiers do not work well, own cascade can be created, but the results are sufficient.

After the mouth is found, cluster is defined from the pixels where the mouth is located in order to narrow our working area further and masking process is performed in our defined color ranges in order to select the red tones in this cluster.

The location of the mouth creates two inputs. The first is the distance of the spoon on the horizontal axis with the user and the second is the height adjustment of the spoon. When the robot reaches the fixed position with the food, the mouth tracking application starts working as described above and the inputs are necessary for reaching the spoon to the mouth.

The first input, i.e. the distance difference in the horizontal axis, is obtained from the difference of the horizontal distance from the center of the frame to the point where the mouth is located in the fixed position of the camera shown in Figure 30 on the left side. The calculation is as follows:

∆X = CX − (x + mx +

mw
2

) , x + mx = X ,

mw
2

=

W
2

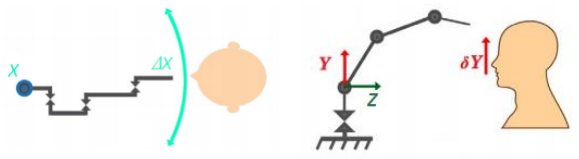
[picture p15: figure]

Figure 30: Rotation of the robot in x-axis(Left) , lifting in y-axis(Right)

Algorithm 1: Panning motion (X direction) adjustment algorithm

if ∆X < −50 pixels then

Panservonew = Panservoold − k;

if ∆X > 50 pixels then

Panservonew = Panservoold + k;

The second input is the difference in distance between the spoon and the mouth, which is the difference between the vertical distance in the middle of the frame and the vertical distance of the mouth. Vertical movements of the camera are represented as in Figure 30 on the right side.

∆Y = CY − (y + my +

mℎ
2

) , y + my = Y ,

mℎ
2

=

H
2

Algorithm 2: Height (Y direction) adjustment algorithm

if ∆Y < −200 pixels then

Ay = Ay − k;

if ∆Y > −100 pixels then

Ay = Ay + k;

Algorithm 2 is realized whether to increase or decrease the height of the spoon or end effector considering ∆Y. Experimentally it is found out that keeping the identified mouth between -200 to -100 pixels gives the proper height needed to feed the food properly. Inverse kinematics equations of a 4 DOF planer robot are used to calculate the new joint angles according to the output by Algorithm 2.

### 3.5.1. Flowchart of the Algorithm

Figure 31: Flowchart of the Algorithm

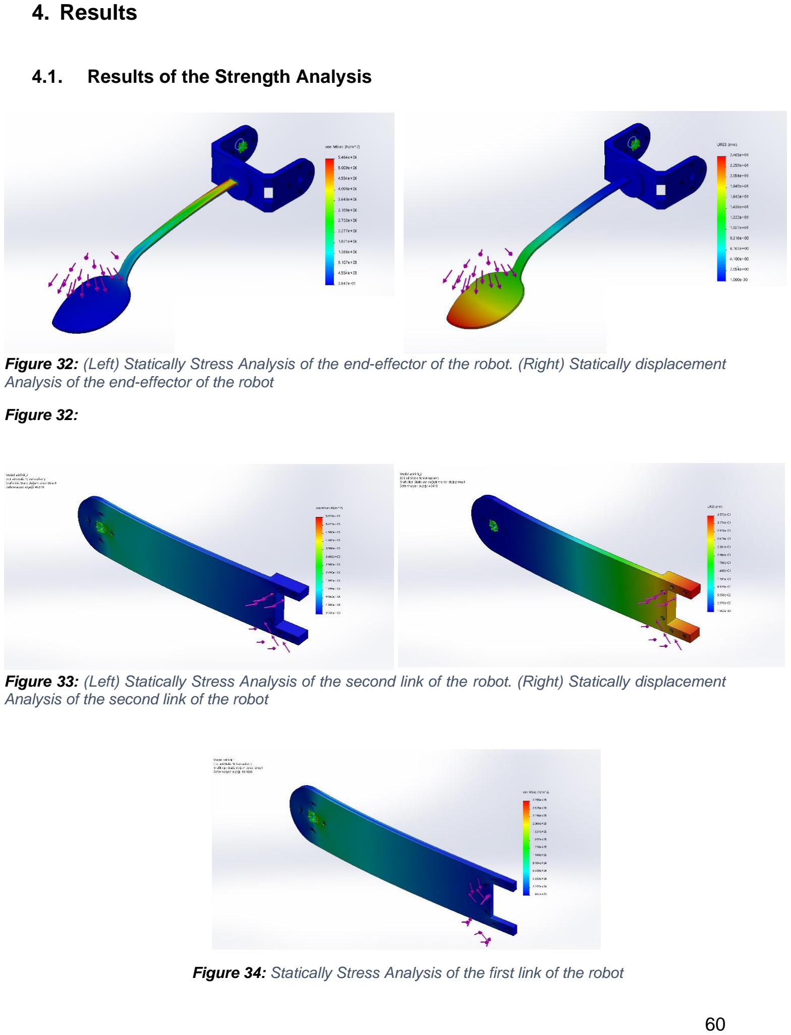
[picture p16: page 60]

### 4. Results

### 4.1. Results of the Strength Analysis

Figure 32: (Left) Statically Stress Analysis of the end-effector of the robot. (Right) Statically displacement Analysis of the end-effector of the robot

Figure 32:

Figure 33: (Left) Statically Stress Analysis of the second link of the robot. (Right) Statically displacement Analysis of the second link of the robot

Figure 34: Statically Stress Analysis of the first link of the robot

### 4.2. Results of the Image Processing

Figure 35: Mouth Position Determined and Shown

As you can see in Figure 35, the program output is demonstrated. The horizontal and vertical distance differences and the location of the opening are clearly indicated.

When the robot arm reaches the desired position range on the x and y axes, the program output is changed in Figure 36. The location of the mouth was found successfully and the position information results were obtained.

Figure 36: Output changes when the position of the mouth is appropriate

### 4.3. Results of the Simulation of the Feeding Assistance Robot

In the previous parts of this document inverse and forward kinematics were investigated. These subjects are also called as the geometry of the robot arm. With these analyses, the mathematical model of the robot arm was reached. These solutions are completely related to the intrinsic of the robot arm.

However, in this part of the project, the main focus was to show that the robot arm can work properly in its workspace. In order to get a properly working robot arm, the robot arm should be able to move from one to another in a smooth way, firstly. In other words, this smooth move problem could be named as trajectory planning. Here trajectory means that the position, velocity and acceleration values of each joint are known at that exact same time. This will provide the robot arm a smooth movement and will make us sure that the system maintains our requirements.

In this part of the project, all of the specified movements were visualized in our simulation environment and relative outputs such as position, velocity, acceleration comparison of solutions that were made in different spaces are recorded. Furthermore, the source codes, mechanical design and assembly files, video record of the simulations and detailed explanations about the steps of implementation of a robot arm in a simulation environment were shared in our team’s GitHub repository [13] so anyone who wants to simulate a robot arm could find this source helpful.

The first thing that was done to create a URDF file from the robot arm’s assembly file which created in SOLIDWORKS, an extension called SolidWorks to URDF Exporter [14] was used to create this URDF file. In this part, choosing joint axes and origins for these joint axes were important. After done with these, relations between links must be assigned with the extension’s easy to use interface. The interface of the SolidWorks to URDF Exporter could be seen in figure 37.

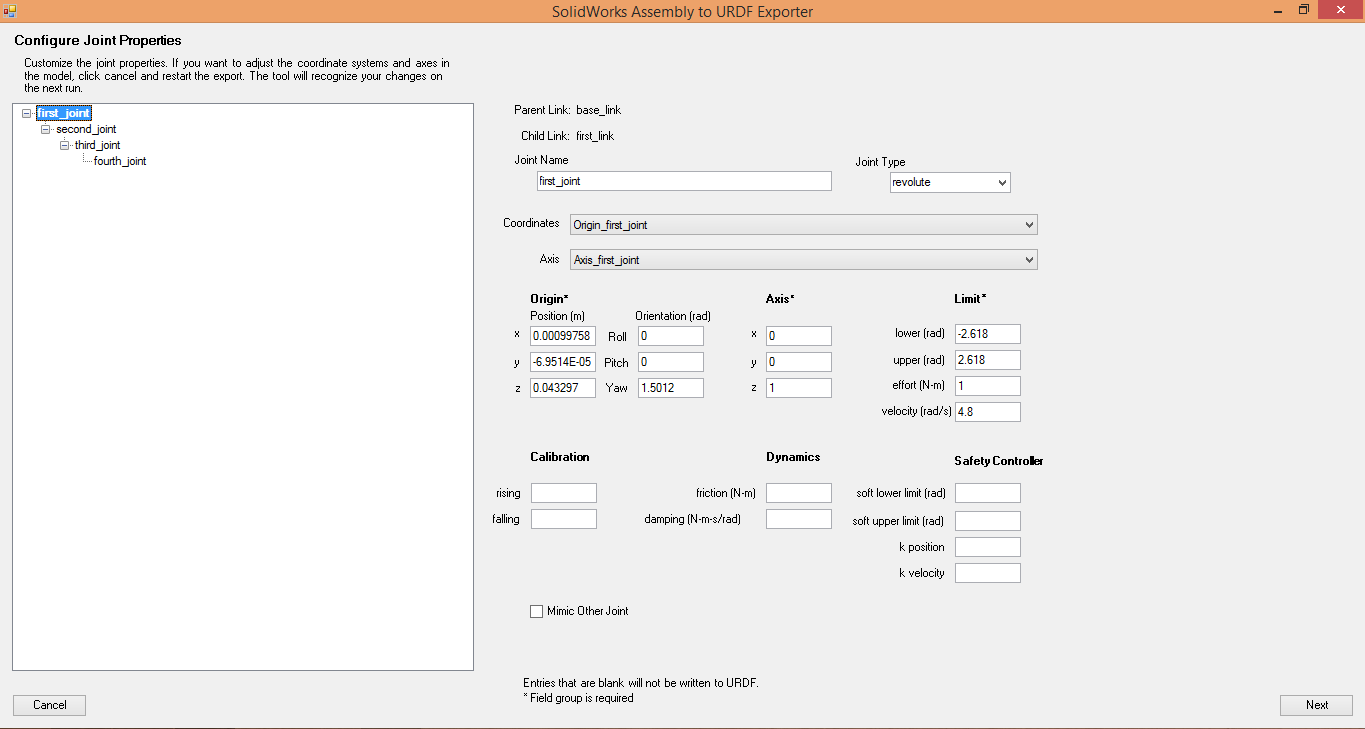
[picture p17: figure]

Figure 37: The interface of the Solidworks to URDF Exporter

After we got the URDF file from Solidworks, the project was ready to be worked on it. For the simulation part, MATLAB and Simulink were used. Especially, a toolbox called Robotics System Toolbox made this simulation available. Robotics System Toolbox provides tools and algorithms for designing, simulating, and testing manipulators, mobile robots, and humanoid robots. For manipulators and humanoid robots, the toolbox includes algorithms for collision checking, trajectory generation, forward and inverse kinematics, and dynamics using a rigid body tree representation [15].
The first step in MATLAB was to show the robot arm in the simulation environment. In figure 38 below you can see the robot arm and the second joint colored in yellow and its positive revolute direction also.

Figure 38: The robot arm in the simulation environment

After the import operation was done the path planning could be done. There are two spaces that we could use in trajectory generation and these are joint space and task spaces. Both of these solutions have pros and cons, for instance, while the joint space provides a faster solution, the task space, on the other hand, provides better handling of obstacles and collisions [16].

To show the difference between these two solution methods, two trajectories from the home position to the middle bowl was investigated. These trajectories were followed by the end-effector of the robot arm. The home position in this situation was just the position as seen in figure 39. Also, the robot moved to a point on top of the bowl. In figure 39 trajectories produced with joint space and task space methods are shown. While the blue line states the task space solution the dotted red line states the joint space solution.

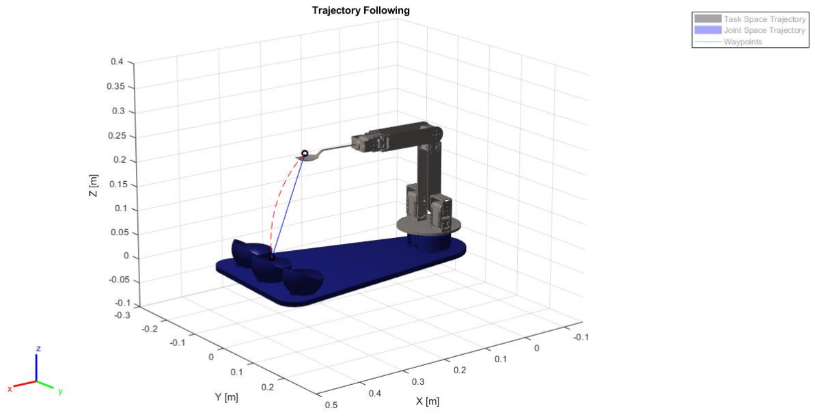
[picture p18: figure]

Figure 39: The comparison between joint space and task space solutions

The main difference between these two solutions was the execution time. In the case of task space solution, inverse kinematics of the robot arm must be solved in every point on the trajectory. However, in the joint space solution, the inverse kinematics of the robot arm has to be solved just in the beginning and endpoints. This trajectory shown in the above figure was completed in four seconds and this movement was divided into 201 timepieces. So our program has to solve inverse kinematics of the robot arm for 201 times. The clear execution time difference could be seen from the results of our system. After the simulation was run in our own computer (core i5, 8GB RAM), the program completed in 14.0772 s for the joint space solution. On the other hand, it took 1192.8127 s (which is nearly 20 minutes) to calculate for task space solution.

The execution time depends on the number which the system has to solve. In the above case, the step time was chosen as 0.02 s which means that inverse kinematics must be solved in every 0.02 s between 0s and 4s. However, it is still possible to get a smooth motion with bigger intervals. For example, when 0.2 s is taken as step time the trajectory was calculated in 112.5419 s with task space solution. However, there wasn’t any clear difference in joint space solution and it took 13.5797 s to solve it. Because our system will always do same motion while reaching the bowls and to the home position and these trajectory planning solutions could be saved and be used in every time task space solutions will be used in our trajectories.

One other reason for choosing the task space solution was that its position plot is differentiable and guarantees a smooth motion. Furthermore, there was no clear difference between task space and joint space as it could be seen in figure 40. This figure illustrates joint positions solved in the task and joint space for all four joints.

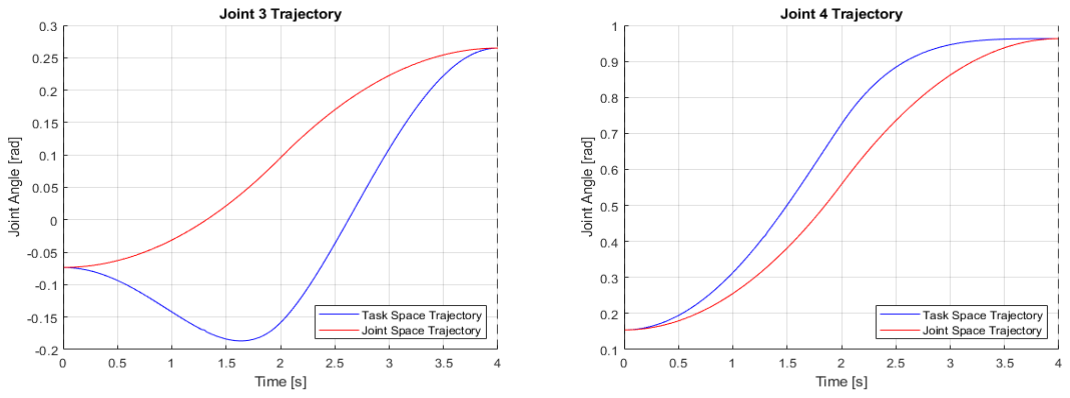
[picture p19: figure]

Figure 40: The comparison of the joint positions produced with joint space and task space for all four joints

The simulation also proved that our servo motors are capable to work properly. As it is seen from figure 41 the maximum angular velocity that the system reached was 0.6 rad/s in the second joint. In this angular velocity, our servo motors can provide 1.69 N ∙ m torque which is obviously higher than our required torque value for that joint which is 0.40 N ∙ m in static conditions. Furthermore, other joints’ angular velocity plots with respect to time, is seen in figure 41.

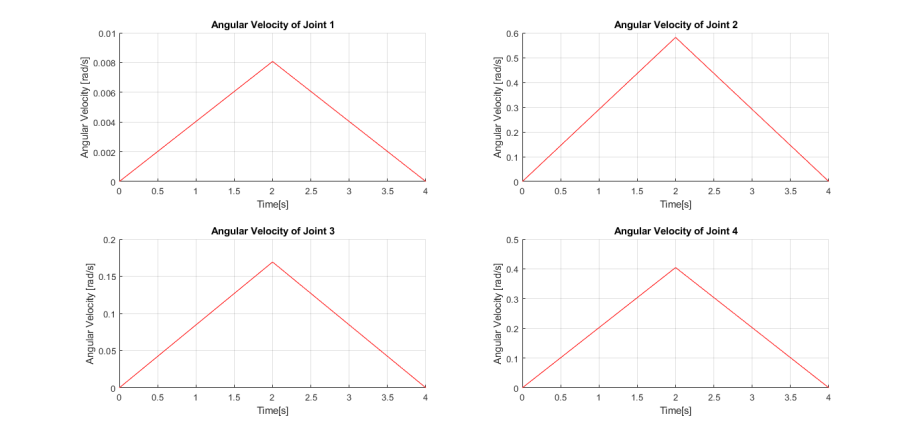
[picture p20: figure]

Figure 41: Angular velocity plots for each joint

Moreover, the angular acceleration of each joint was investigated, it is seen in figure 42 when these acceleration values put into the dynamics analyses that mentioned earlier, it could be proven that our servo motors could provide these torque values. Also, it is seen from these figures that there are no sudden acceleration changes which could affect the smoothness of the motion. According to these plots, the maximum sudden change in the acceleration value is 0.6 rad/s

2

Figure 42: Angular acceleration plots for each joint

After the trajectories were explored from the home position to the bowl in the middle, movements from the home position to the bowls in the right and left side of the base plane were explored. However, the same code used for the simulation of previous trajectories we talked about in the above couldn’t be used because the end-effector also has to have an orientation in these new trajectories. In order to provide this orientation at the end of this path, our system has to calculate the orientation matrices in addition to the position vector and must solve the inverse kinematics with respect to the whole 4 × 4 transformation matrix. It is seen in the equation (1) that a transformation matrix without any rotation and in the equation (2) that a transformation matrix with a rotation matrix.

T = [

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
] | (1)

T = [
R3×3

px
py
pz
0 0 0 | 1
] | (2)

As it can be seen from figure 43 the end-effector must have a 15 degrees rotation in the z-axis and must have no rotation in other axes. Also, it could be observed from the figure clearly that the system solved the rotations and positions at the same time for each step.

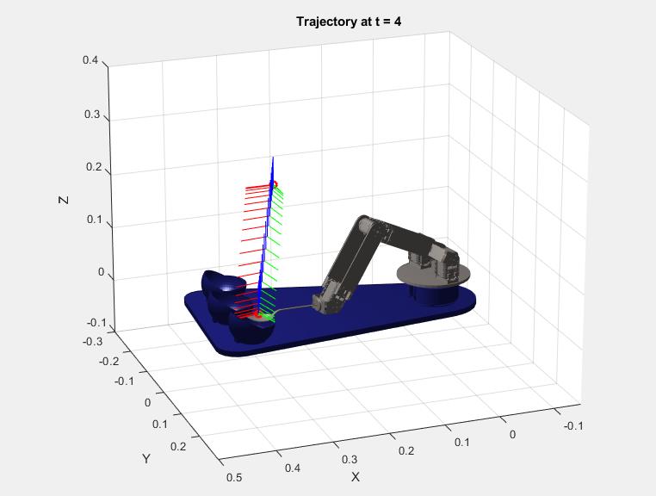
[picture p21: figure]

According to our settings, the end-effector moves from home position to the bowl in the right in four seconds. And, the time interval was assigned as 0.2 s which means there were just 21 points that our system has to solve the inverse kinematics in these points. Because we can save the data produced by the solution of inverse kinematics the execution time wasn’t considered as a constraint. For that reason, just the task space solution was used to creation of the trajectory. In the case 0.2 s was used as time interval the system was able to create the trajectory in 130.785 s which is reasonable execution time. Also, 0.1 s was tested for the comparison and in that case, our system was able to create the trajectory in 237.19 s.

In addition to these trajectories, the trajectory from home position to the bowl in the left was simulated. As it could be seen from figure 44 it is just the mirrored pair of the previous trajectory. Furthermore, the execution times were nearly the same for both of these trajectories. The only difference in this motion was that the orientation of the end-effector at the endpoint was -15 degrees.

Figure 44: End-effector with rotation on top of the bowl in the right

Figure 43: End-effector with rotation on the endpoint(left), end-effector in the home position

Totally, six different trajectories for the robot arm were created and simulated in Matlab. To be able to evaluate these, firstly, the assembly file of the robot arm was exported to a URDF file. After that, some arrangements were made in the Matlab environment to control the robot using functionalities of the Robotics System Toolbox. Then, waypoints that the end-effector of the robot must be followed were given to our system and also rotations in those waypoints were given to the system. The following was telling the system the trajectory planning method. In our case trapezoidal trajectory planning was chosen and tested, other trajectory planning methods could be chosen. After the system was run and created trajectories the final step was to run the simulation part of the code.

After simulation results were obtained, the controller design was investigated. In our project, servo motors were used as a rotary actuator. In that case, there is no need to design a controller because servo motors used in our project contains its own controller circuit inside of it. If somebody needs to control these motors, s/he just needs to install its software development kit [17] and control them with couple lines of codes. However, in the scope of the Mechatronic System Design course design of a controller is a must. For this reason, a basic PID controller was developed in the Simulink environment to control the position output as seen in figure 45.

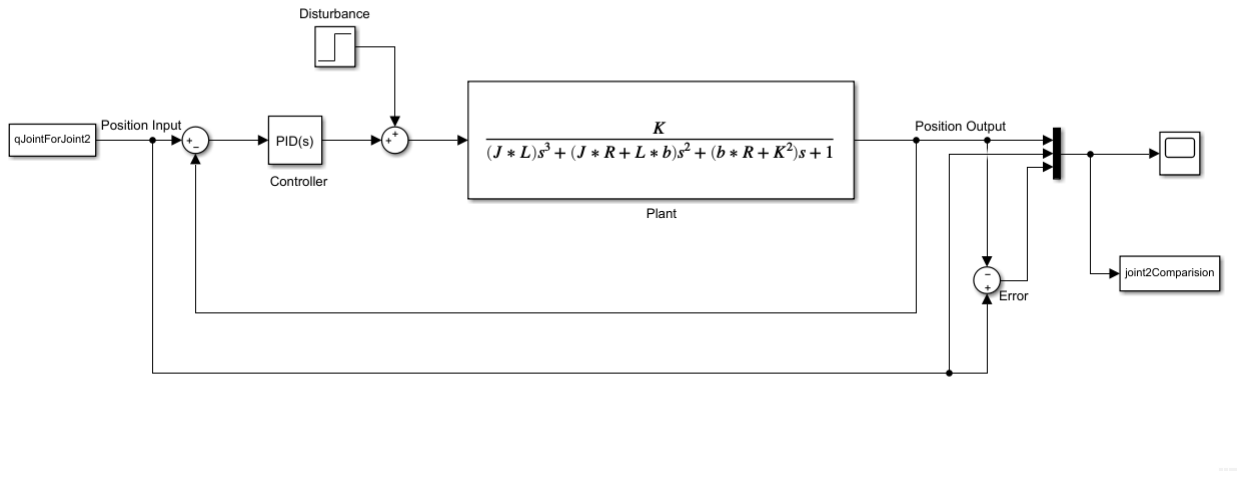
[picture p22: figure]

Figure 45: Simulink blocks for position control

In this controller design, some assumptions were made. As it has known a servo motor is comprised from a DC motor, gears and a controller circuit. And, to design the Plant part of the controller some physical parameters (like the moment of inertia of the rotor, motor torque constant e.g.) must be known exactly. However, there was no information on the producer side about any of this parameter. Even though there are some written programs in Simulink to find these parameters’ values, we couldn’t reach those because we haven’t been able to buy the connection part for the servo motor.

Instead, some constants were used to simulate the servo motor These values were derived by experiment from an actual motor in Carnegie Mellon University's undergraduate controls lab [18].
(J) Moment of inertia of tℎe rotor 3.2284 ∙ 10⁻⁶ kg ∙ m²

(b) Motor viscous friction constant 3.5077 ∙ 10⁻⁶N ∙ m ∙ s

(Kb

) Electromotive force constant 0.0274 V/rad/s

(Kt

) Motor torque constant 0.0274 N ∙ m/Amp

(R) Elecrical resistance 4 Oℎm

(L) Electrical Inductance 2.75 ∙ 10⁻⁶H

The transfer function for the PID controller was like that:

C(s) = Kp +

Ki
s

+ Kds =

Kds

2 + Kps + Ki
s

This PID controller’s parameter was chosen with the help of Simulink’s PID Tuner App, and the best parameters for our system were given like these:

Kp = 324, Ki = 32186,Kd = 0.57

As it has seen from the above figure, the position input, the output position and the error between these two signals were plotted in the same scope. This scope could be seen in figure 46. As seen from this figure the controller worked accurately and produced an output signal as exactly the same with the input signal. Figure 46 illustrates signals for the third joint, in this case, the blue line represents the output while the red line represents the input signal. The error was about 0.01 rad at the beginning of the movement.

Figure 46: Comparison of input, output signals and the error between two of them for third joint

Also, the controller characteristic without auto-tuning was observed, in this case, PID parameters were investigated by plots of the output for a given step input. With the help of many loops which enabled us to test many cases, our controller had a sufficient step response. And, the application of this controller for the second joint could be seen in figure 47.

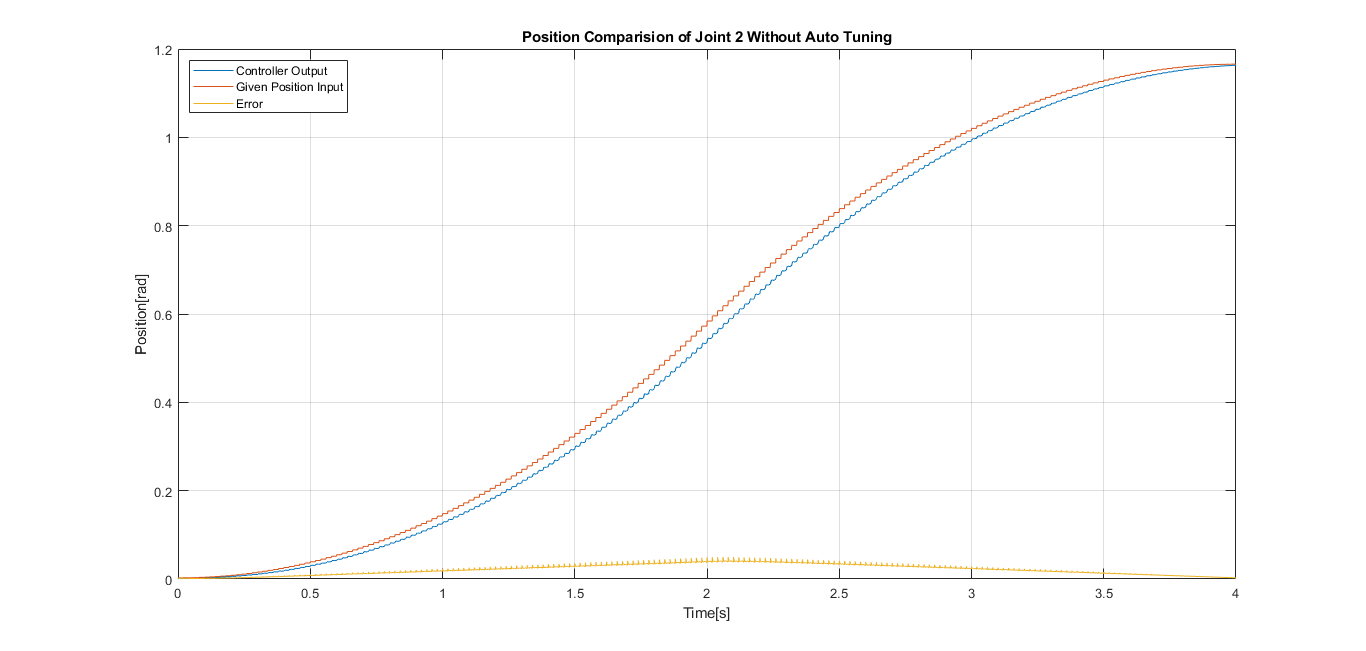
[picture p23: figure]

Figure 47: Comparison of input, output signals and the error between two of them for second joint

Also, one other simulation environment was created for the test of the controllers developed for the motors. In order to evaluate this simulation, the assembly file of the robot arm was converted to a Simulink structure by using the Simscape Multibody Link add-on. After this conversation, the robot arm was seen in the Simulink environment as in figure 48.

Figure 48: The structure in the Simulink environment, which represents the robot arm.

After this structure was obtained, the next step was to convert this structure to a subsystem for simplicity. This subsystem was created with determining its input and output ports. In this subsystem, the position input signals which were provided by a PID controller were the input signals. The position output signals and the torque values were the output values of the system as it would be seen in figure 49.

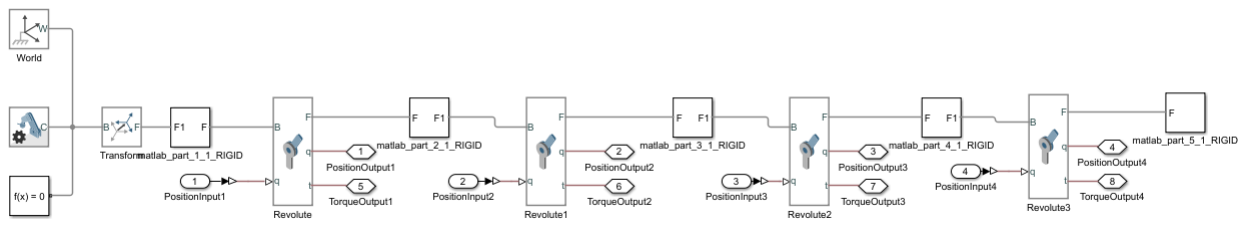
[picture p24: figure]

Figure 49: The structure of the subsystem

Then all four joints must be controlled by a controller. In our case, the PID controller was chosen because it provides proportional (P), integral (I) and derivate (D) control terms. All of the PID controllers were added before the input terminal of the subsystem as it could be seen in figure 3. The same parameters were used in all four PID controller because it was assumed that all joints were actuated by the same servo motor. And, these are the parameters obtained by the PID Tuner App in MATLAB:
Kp = 2, Ki = 14200,Kd = 6.50 × 10⁻⁵

Also, the comparison plots were obtained which shows the difference between the input signal and output signal. Other than these plots one plot was added to the system to show the joints torque values as it could be seen in figure 50.

Figure 50: The overall system to control the robot arm.

From this simulation, it could be said that our PID controller was pretty sufficient to meet the system’s requirements to be controlled. This result is also clearly seen in figure 51. This figure represents the comparison of the reference (input) and output position signals and as it is seen from that these two signals are exactly the same.

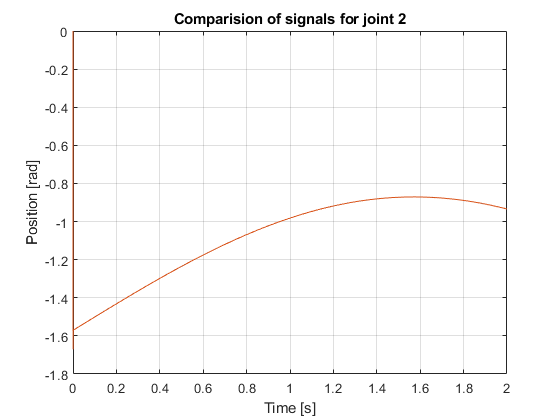
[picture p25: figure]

Figure 51: The comparison of reference and output signals for the second joint.

Moreover, this simulation gives the torque values which are required to move the desired joint position. And, the maximum torque was required in the second joint and it was around the 0.22 N ∙ m which is clearly lower than the torque values that our servo motors could supply.

### 5. Cost and Product Backlog Items Tables

### 5.1. Cost Table

Table 6: Cost Table of the Feeding Assistance Robot
Product Name | Brand/Model | Quantity | Cost (₺)
Servo Motors | Dynamixel AX18-A | 2 pieces | 1541,82
Servo Motors | Dynamixel AX12-A | 3 pieces | 1094,34
USB to TTL Converter | USB2Dynamixel | 1 piece | 267,17
TTL Cables | Robotis 3P 140mm | 10 pieces | 767,6
Camera | Logitech C310 HD Webcam | 2 pieces | 541,78
Lipo Battery | ProFuse 11.1V 3S 2800 mAh | 1 piece | 200,82
3D Printed Parts | colorFabb | 1 piece | 227,99
Bolts | Robotis M2 | 72 pieces | 28,74
Bolts | Robotis M3 | 6 pieces | 28.74
Caster Wheel | Robotistan | 3 pieces | 42,12
Total Cost: | | | 4712,38

### 5.2. Product Backlog Items Table

Table 6: Product Backlog Items Table of the Feeding Assistance Robot
Sprint Number | Work in Progress(WIP) | Tasks
1 | Upper Side Manufacturing of the robotic arm | Manufacturing of the Base Retainer

Manufacturing of the First Link

Manufacturing of the Second Link

Manufacturing of the Bottom Plate

Manufacturing of the Connecting Kit

Design of the Spoon

Check the Dynamic Analysis

Control of the servo motors

Communications with computer

Connection with robot

Tested of the servo motors | Testing the movement
3 | Manufacturing of other parts of the robotic arm | Manufacturing of the Base Plate

Manufacturing of the Bowl

Manufacturing of the Connecting Holder

Manufacturing of the Spoon
General integration of the system | Integrations of the overall system
4 | Integration of the Cameras | To locate the camera to suitable position without change the center of gravity to obtain more accurate, smooth motion

Connection with computer

Testing the camera

Design of the GUI(Graphical User Interface)

Coding of each actions for each buttons

Testing of eye-tracking libraries

Integrations of eye-tracking with our GUI

Test of the system with development team

Test of the system with patients

Mouth-Tracking integration to robotic arm

Output of the mouth-tracking algorithm used in the servo motor controls to obtain motions on x,y axes.

Creating the open-closed mouth detection and testing feeding operation

7

Design of User-Interface

Integration of eye-tracking

Testing of prototype

Redesign of the end-effector

Integration of the servo motors
2

5

6

Note: Each Sprint will take two weeks.

### 6. Conclusion

For people who have upper limb disabilities, this feeding robot design will be helpful so much. It won’t only give back their independence back to them, it also will reduce the need for a caregiver. In conclusion, in the scope of this project, the mechanical design of a 4-DOF robotic arm was done to serve as a feeding assistant robot, the forward and inverse kinematics of it were developed. Then dynamical analyses of this robot were done. After these, each part of the robot arm design was subjected to strength analysis. A simulation of the robot arm to show that it is capable of working in its workspace was developed. Finally, the mouth tracking feature of the system was written, and it was tested successfully.

These works are the things that have been done during the fall semester for the scope of the Mechatronics System Design course. In the next semester, this design will be realized in the scope of the Senior Design course. First, the servo motors will be tested for trajectory following. Then, each part of the design will be manufactured with 3D printers. After that, mechanical and electrical integration will be held. Next, each different trajectory for each of the bowls will be tested. Finally, the eye-tracking and mouth tracking software will be integrated with the trajectory following software.
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

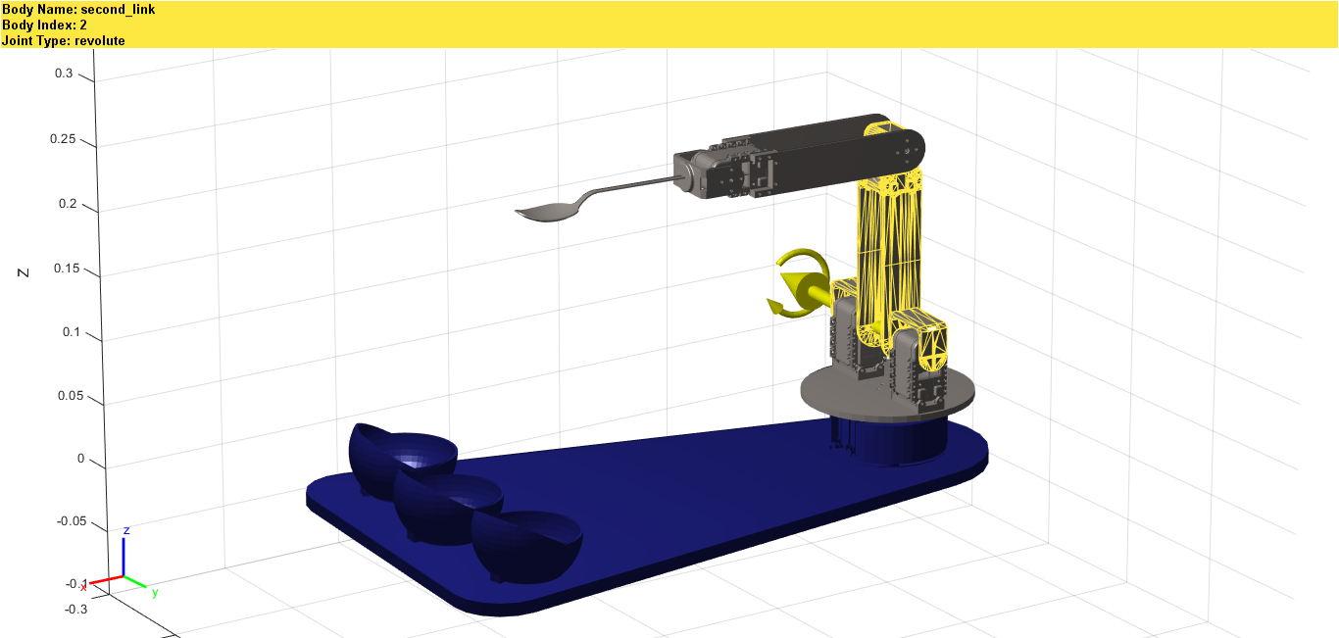
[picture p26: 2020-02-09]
simulationOfTheRobotArm/robotArmInSımulationEnv.png

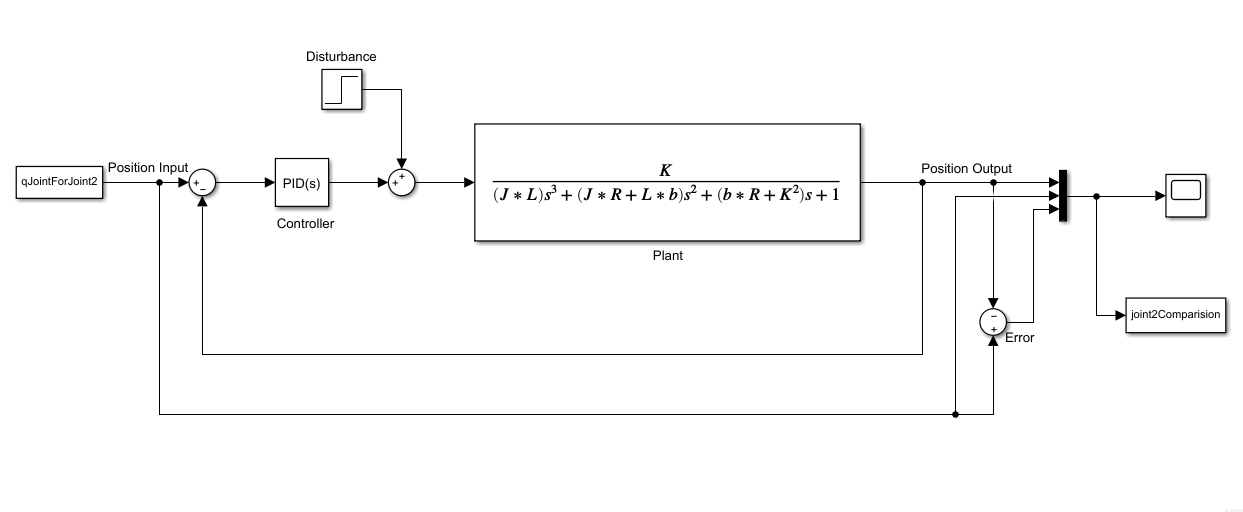
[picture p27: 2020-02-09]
simulationOfTheRobotArm/SimulinkFigureJoint2.PNG

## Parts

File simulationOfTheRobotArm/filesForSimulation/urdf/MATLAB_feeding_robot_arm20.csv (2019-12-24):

Link Name | Center of Mass X | Center of Mass Y | Center of Mass Z | Center of Mass Roll | Center of Mass Pitch | Center of Mass Yaw | Mass | Moment Ixx | Moment Ixy | Moment Ixz | Moment Iyy | Moment Iyz | Moment Izz | Visual X | Visual Y | Visual Z | Visual Roll | Visual Pitch | Visual Yaw | Mesh Filename | Color Red | Color Green | Color Blue | Color Alpha | Collision X | Collision Y | Collision Z | Collision Roll | Collision Pitch | Collision Yaw | Collision Mesh Filename | Material Name | SW Components | Coordinate System | Axis Name | Joint Name | Joint Type | Joint Origin X | Joint Origin Y | Joint Origin Z | Joint Origin Roll | Joint Origin Pitch | Joint Origin Yaw | Parent | Joint Axis X | Joint Axis Y | Joint Axis Z | Limit Effort | Limit Velocity | Limit Lower | Limit Upper | Calibration rising | Calibration falling | Dynamics Damping | Dynamics Friction | Safety Soft Upper | Safety Soft Lower | Safety K Position | Safety K Velocity
base_link | 0.194934821629088 | -0.0135833956377986 | 0.00709237953021339 | 0 | 0 | 0 | 1.2996491336163 | 0.00513241757298595 | 0.000909915765740639 | -9.70075439247577E-06 | 0.0181269922660767 | 6.78255105158956E-07 | 0.0231749776351054 | 0 | 0 | 0 | 0 | 0 | 0 | package://MATLAB_feeding_robot_arm20/meshes/base_link.STL | 0.12156862745098 | 0.129411764705882 | 0.52156862745098 | 0.35 | 0 | 0 | 0 | 0 | 0 | 0 | package://MATLAB_feeding_robot_arm20/meshes/base_link.STL |  | base_plate-1;bowl-1;bowl-2;bowl-3;base_retainer-1;servo_motor-1;connecting_holder_2-2;connecting_holder_1-2 | Origin_global |  |  |  | 0 | 0 | 0 | 0 | 0 | 0 |  | 0 | 0 | 0
first_link | -5.49706873415783E-08 | 2.4712752783821E-09 | 0.0262538101159052 | 0 | 0 | 0 | 0.159544218113454 | 9.21738994783716E-05 | 4.43464740263406E-09 | -7.30311926145205E-13 | 0.000113290154480954 | -3.08656348752115E-12 | 0.000174389664929604 | 0 | 0 | 0 | 0 | 0 | 0 | package://MATLAB_feeding_robot_arm20/meshes/first_link.STL | 0.647058823529412 | 0.619607843137255 | 0.6 | 1 | 0 | 0 | 0 | 0 | 0 | 0 | package://MATLAB_feeding_robot_arm20/meshes/first_link.STL |  | servo_motor_horn-1;bottom_plate-1;servo_motor-3;servo_motor-2 | Origin_first_joint | Axis_first_joint | first_joint | revolute | 0.00099758 | -6.9514E-05 | 0.043297 | 0 | 0 | 1.5012 | base_link | 0 | 0 | 1 | 1 | 4.8 | -2.618 | 2.618
second_link | -3.90671112193231E-07 | 0.0857335900702113 | 0.000293778750700397 | 0 | 0 | 0 | 0.08126049056897 | 5.30107210326389E-05 | -2.36532041707882E-10 | 2.21591417779484E-09 | 1.32852672838446E-05 | 1.77521297582527E-07 | 5.00305762180477E-05 | 0 | 0 | 0 | 0 | 0 | 0 | package://MATLAB_feeding_robot_arm20/meshes/second_link.STL | 0.647058823529412 | 0.619607843137255 | 0.6 | 1 | 0 | 0 | 0 | 0 | 0 | 0 | package://MATLAB_feeding_robot_arm20/meshes/second_link.STL |  | servo_motor_horn-3;connecting_kit-1;link_1-3;servo_motor_horn-2;connecting_kit-2;link_1-2;servo_motor-4 | Origin_second_joint | Axis_second_joint | second_joint | revolute | 0 | 0 | 0.055203 | 1.5708 | 0 | -1.5708 | first_link | 0 | 0 | -1 | 1 | 4.8 | -2.618 | 2.618
third_link | 0.101673492894517 | 4.64579096498552E-07 | 0.000605967892427892 | 0 | 0 | 0 | 0.0702571061766664 | 8.92340768563915E-06 | 1.88602114898204E-10 | 1.92580071515587E-07 | 5.8728277457127E-05 | -2.22078239798901E-09 | 5.97549761871198E-05 | 0 | 0 | 0 | 0 | 0 | 0 | package://MATLAB_feeding_robot_arm20/meshes/third_link.STL | 0.647058823529412 | 0.619607843137255 | 0.6 | 1 | 0 | 0 | 0 | 0 | 0 | 0 | package://MATLAB_feeding_robot_arm20/meshes/third_link.STL |  | servo_motor_horn-4;link_2-2;link_3-2;servo_motor-5 | Origin_third_joint | Axis_third_joint | third_joint | revolute | 0 | 0.1472 | 0 | 0 | 0 | 0 | second_link | 0 | 0 | 1 | 1 | 4.8 | -2.168 | 2.618
fourth_link | 0.0324387698007119 | -0.00144386213516617 | 0.00282945586620664 | 0 | 0 | 0 | 0.0108011745182262 | 2.74708574332677E-06 | 1.59942953762279E-06 | -5.70280999936005E-08 | 2.28051195237262E-05 | 2.7777092394106E-09 | 2.10473200080076E-05 | 0 | 0 | 0 | 0 | 0 | 0 | package://MATLAB_feeding_robot_arm20/meshes/fourth_link.STL | 0.647058823529412 | 0.619607843137255 | 0.6 | 1 | 0 | 0 | 0 | 0 | 0 | 0 | package://MATLAB_feeding_robot_arm20/meshes/fourth_link.STL |  | servo_motor_horn-5;manipulator-1 | Origin_fourth_joint | Axis_fourth_joint | fourth_joint | revolute | 0.1472 | 0 | 0 | 0 | 0 | 0 | third_link | 0 | 0 | 1 | 1 | 4.8 | -2.618 | 2.618

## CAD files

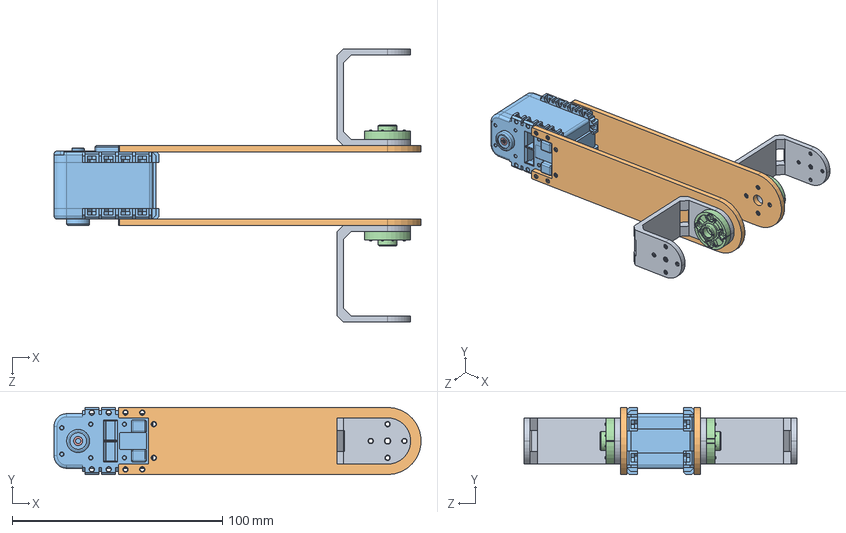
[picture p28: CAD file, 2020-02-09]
CADFiles/matlab_part_3.SLDASM
174.6 x 32.0 x 130.0 mm
connecting_kit x 2
link_1 x 2
servo_motor
servo_motor_horn x 2
idled_revoluted_piece

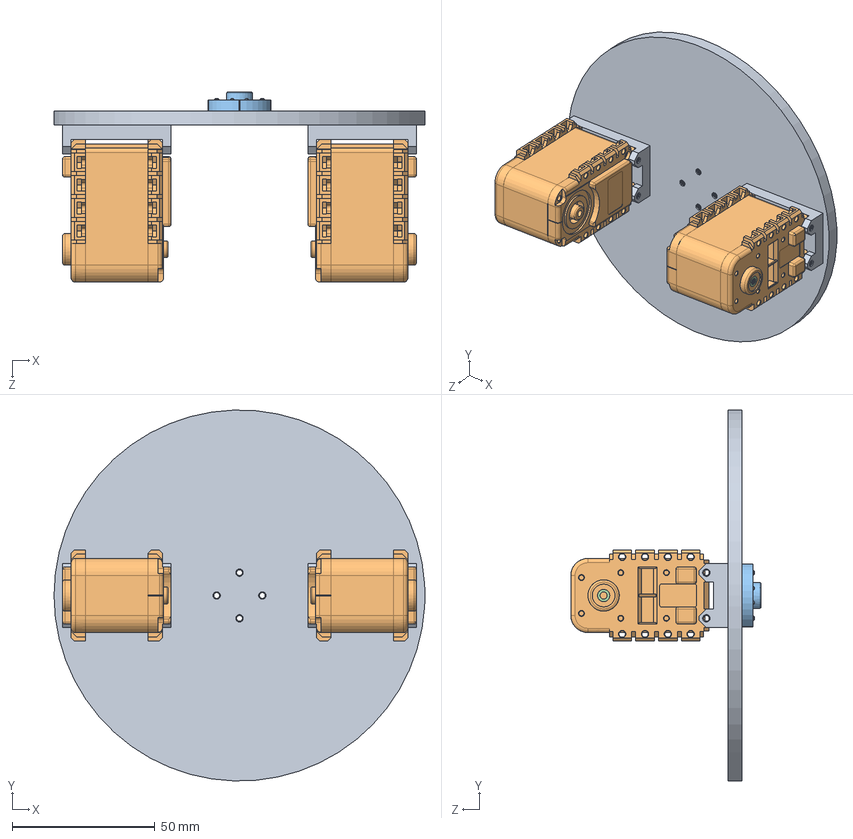
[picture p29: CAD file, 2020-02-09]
CADFiles/matlab_part_2.SLDASM
130.0 x 129.9 x 66.7 mm
bottom_plate
servo_motor x 2
servo_motor_horn
idled_revoluted_piece x 2

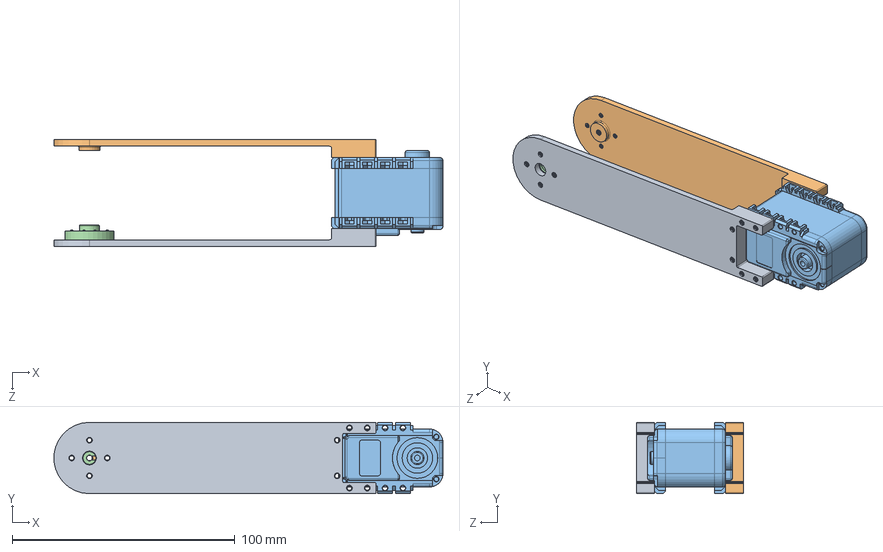
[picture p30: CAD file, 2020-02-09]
CADFiles/matlab_part_4.SLDASM
174.6 x 32.0 x 48.0 mm
link_2
link_3
servo_motor
servo_motor_horn
idled_revoluted_piece

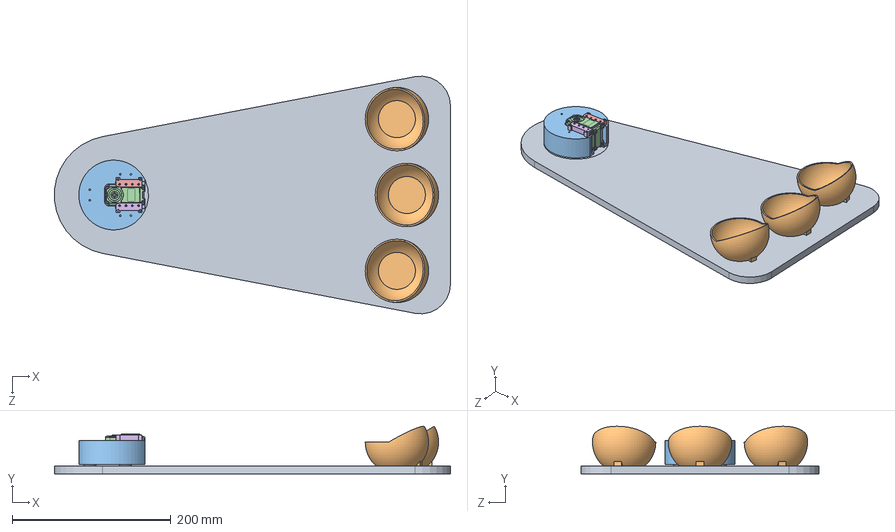
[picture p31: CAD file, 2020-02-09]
CADFiles/matlab_part_1.SLDASM
499.7 x 60.0 x 299.9 mm
base_plate
bowl x 3
base_retainer
servo_motor
connecting_holder_1
connecting_holder_2

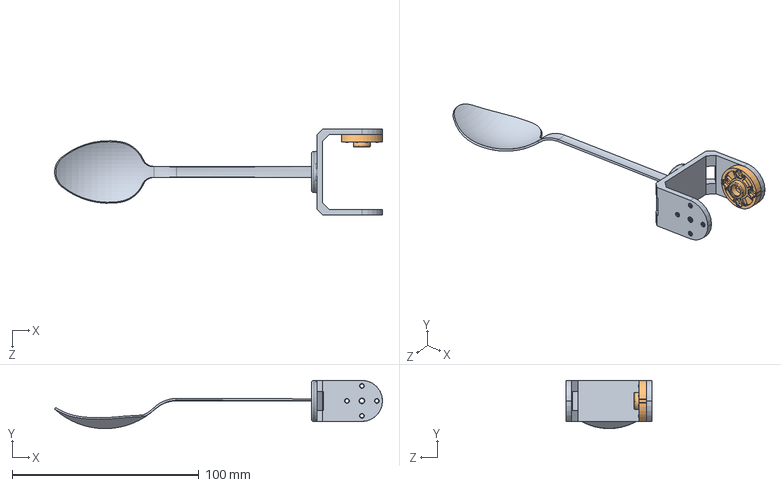
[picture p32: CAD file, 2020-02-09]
CADFiles/matlab_part_5.SLDASM
175.5 x 25.8 x 46.0 mm
manipulator
servo_motor_horn

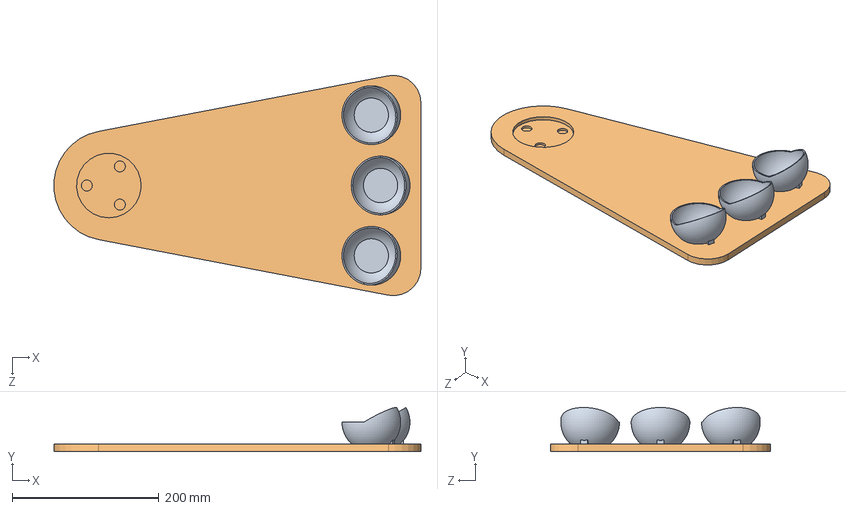
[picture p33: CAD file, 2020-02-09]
CADFiles/base_bowl_assemble.SLDASM
499.7 x 60.0 x 299.9 mm
bowl x 3
base_plate

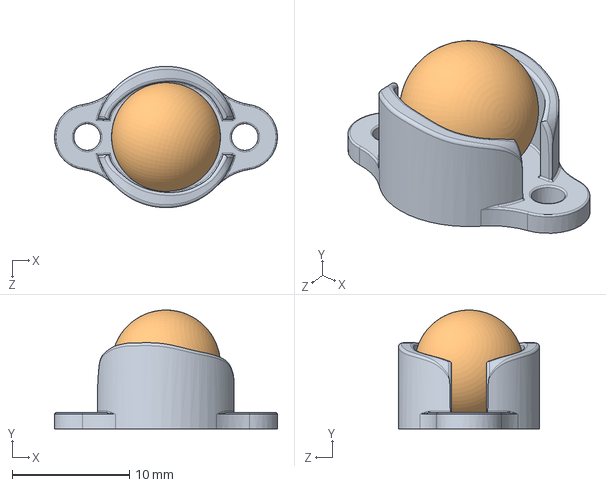
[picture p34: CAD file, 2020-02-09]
CADFiles/wheel_assemble.SLDASM
19.1 x 10.2 x 12.1 mm
base
ball

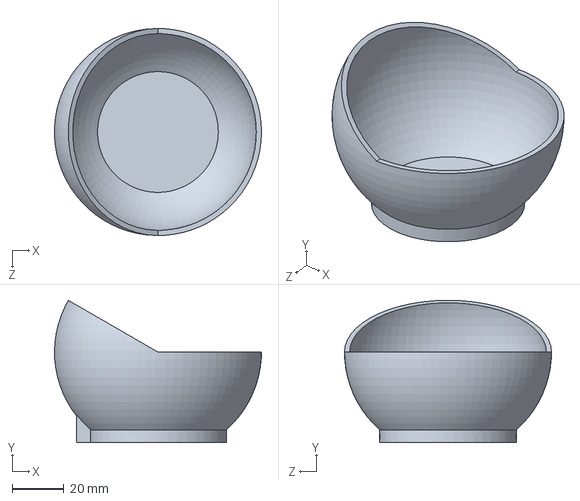
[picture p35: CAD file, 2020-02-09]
CADFiles/bowl.SLDPRT
80.0 x 55.0 x 80.0 mm

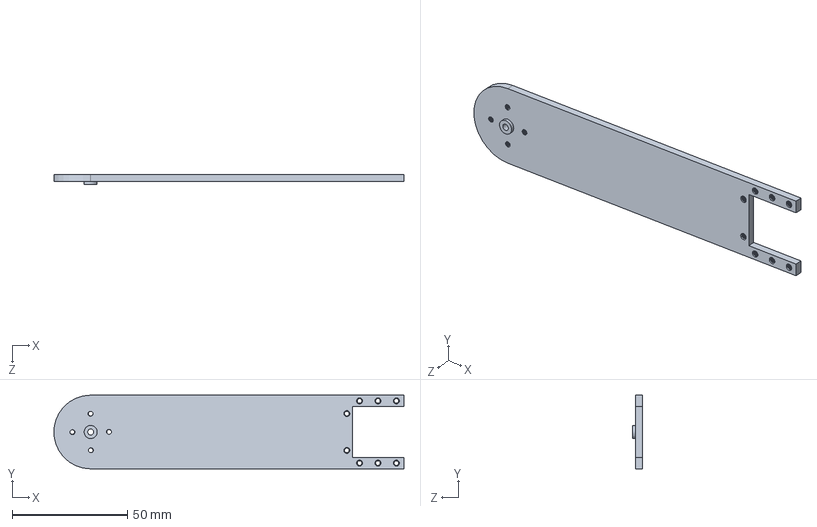
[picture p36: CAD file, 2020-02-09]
CADFiles/GEREKSİZ/link_2.SLDPRT
151.9 x 32.0 x 4.30 mm

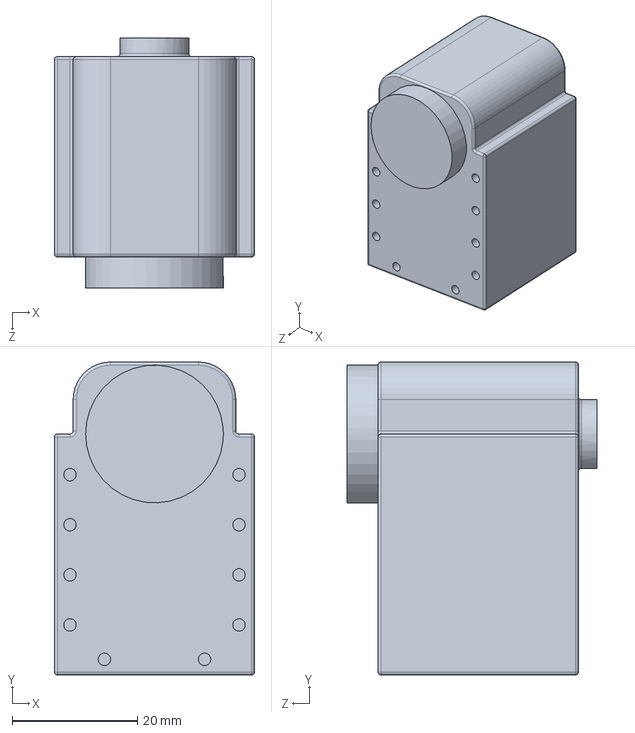
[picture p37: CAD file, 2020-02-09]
CADFiles/servo_motor/deneme_servo_v1.SLDPRT
32.0 x 50.0 x 40.0 mm

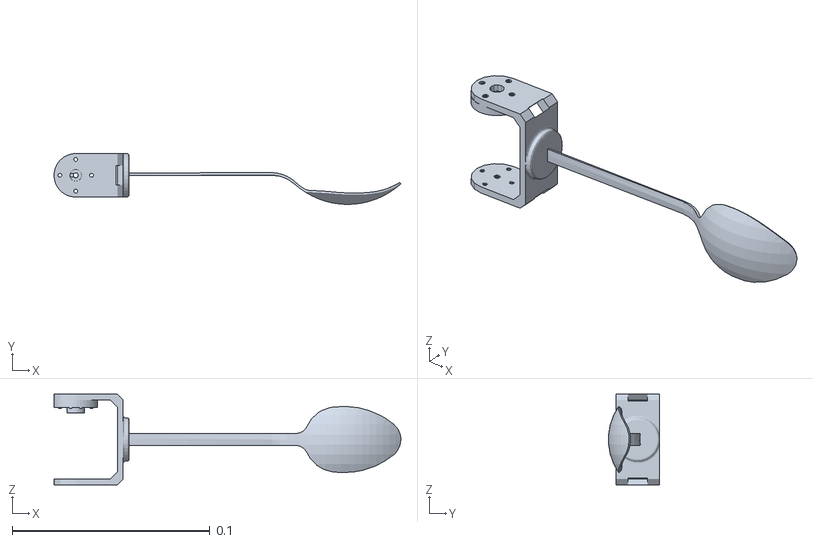
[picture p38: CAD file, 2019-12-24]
simulationOfTheRobotArm/filesForSimulation/meshes/fourth_link.STL
0.176 x 0.0257 x 0.046

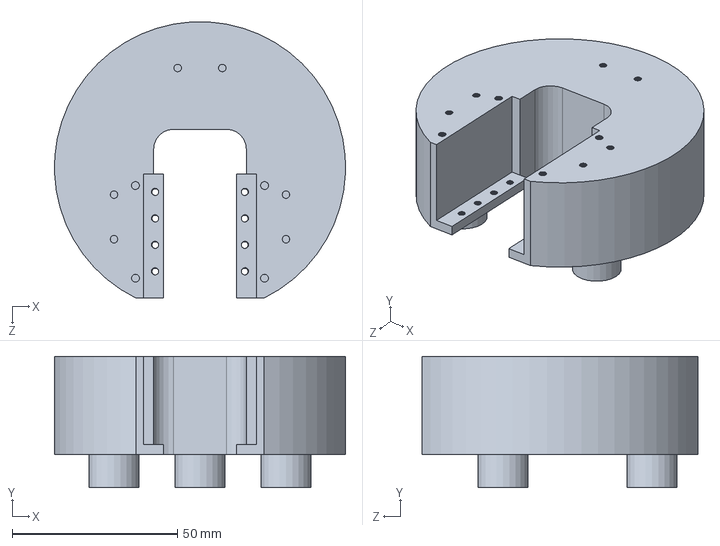
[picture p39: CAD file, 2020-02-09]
CADFiles/GEREKSİZ/base_yedek.SLDPRT
87.9 x 39.7 x 83.4 mm

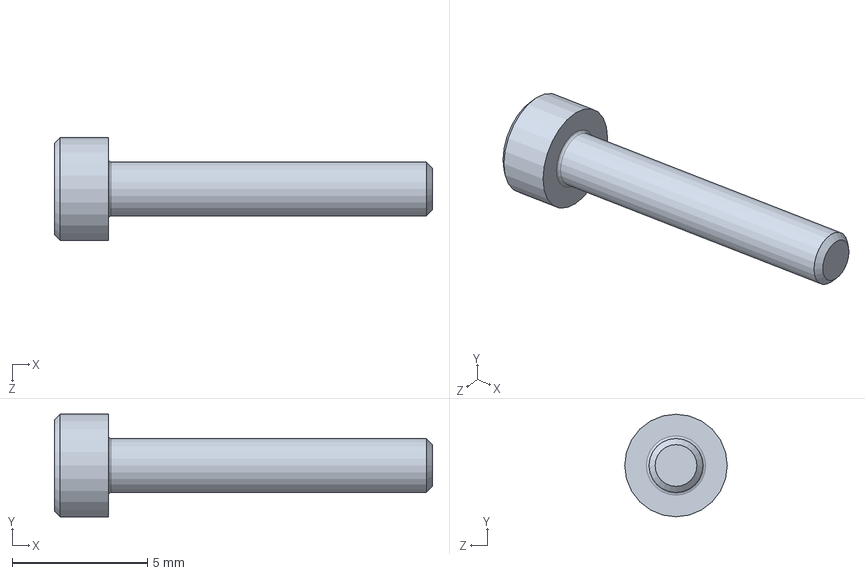
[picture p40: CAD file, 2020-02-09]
CADFiles/vida_length12mm-diameter2mm.SLDPRT
14.0 x 3.80 x 3.80 mm

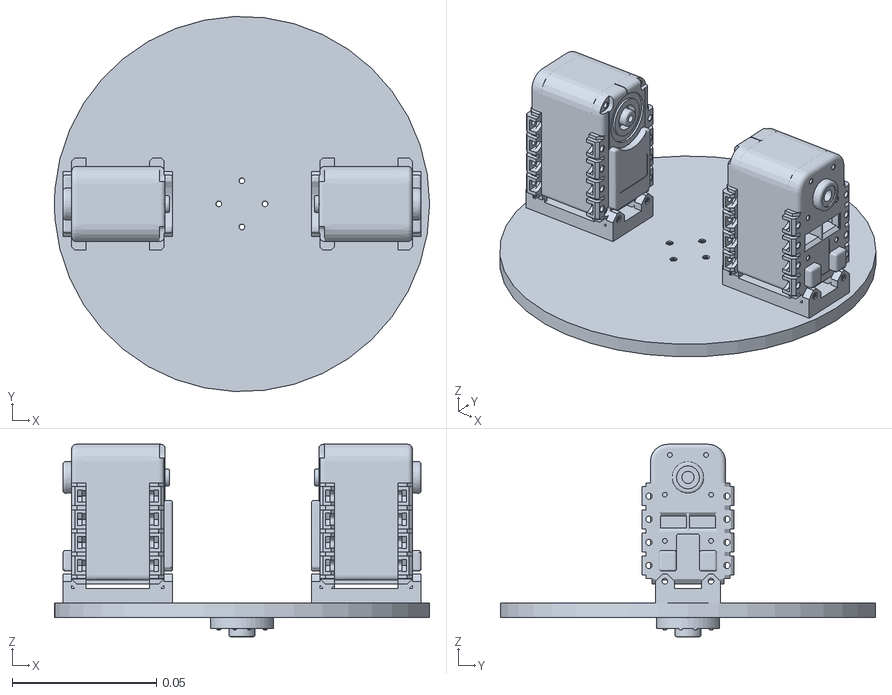
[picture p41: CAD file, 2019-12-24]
simulationOfTheRobotArm/filesForSimulation/meshes/first_link.STL
0.13 x 0.13 x 0.0667

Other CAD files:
CADFiles/GEREKSİZ/base_deneme.SLDPRT
CADFiles/wheel_ball.SLDPRT
CADFiles/idled_revoluted_piece.SLDPRT
CADFiles/manipulator.SLDPRT
CADFiles/base_plate.SLDPRT
CADFiles/base_retainer.SLDPRT
CADFiles/bottom_plate.SLDPRT
CADFiles/connecting_holder_1.SLDPRT
CADFiles/connecting_holder_2.SLDPRT
CADFiles/connecting_kit.SLDPRT
CADFiles/link_1.SLDPRT
CADFiles/link_2.SLDPRT
CADFiles/link_3.SLDPRT
CADFiles/matlab_part_2.SLDPRT
CADFiles/matlab_part_5.SLDPRT
CADFiles/servo_motor.SLDPRT
CADFiles/servo_motor_horn.SLDPRT
CADFiles/technical_drawing/Servo Motor Assemble.SLDDRW
CADFiles/technical_drawing/base_plate.SLDDRW
CADFiles/technical_drawing/base_retainer.SLDDRW
CADFiles/technical_drawing/bottom_plate.SLDDRW
CADFiles/technical_drawing/bowl.SLDDRW
CADFiles/technical_drawing/connecting_holder.SLDDRW
CADFiles/technical_drawing/connecting_kit.SLDDRW
CADFiles/technical_drawing/link_1.SLDDRW
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

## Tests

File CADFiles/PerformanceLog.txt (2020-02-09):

Preparing to transfer data:  0 hr 0 min 0 sec
Processing material properties:  0 hr 0 min 0 sec
Processing element groups:  0 hr 0 min 0 sec
Processing drop test gap nodes:  0 hr 0 min 0 sec
Updating thickness for shell regions:  0 hr 0 min 0 sec
Processing rconst for elements:  0 hr 0 min 0 sec
Processing egroups:  0 hr 0 min 0 sec
Transferring loads and boundary conditions:  0 hr 0 min 0 sec
Generating body pairs to check contact:  0 hr 0 min 0 sec
Generating contacts:  0 hr 0 min 0 sec
Number of Contacts: 0
Transfer SL1 data:  0 hr 0 min 0 sec
Generate simplified contact data:  0 hr 0 min 0 sec
Generate more accurate contact data:  0 hr 0 min 0 sec
Number of contact data: 0
Transfer beam/joint contact data:  0 hr 0 min 0 sec
Transferring other special loads:  0 hr 0 min 0 sec
Transferring bearing loads:  0 hr 0 min 0 sec
Transferring mass elements:  0 hr 0 min 0 sec
Transferring point loads:  0 hr 0 min 0 sec
Transferring distributed beam loads:  0 hr 0 min 0 sec
Transferring rigid bodies:  0 hr 0 min 0 sec
Transferring component no penetration:  0 hr 0 min 0 sec
Writing Data:  0 hr 0 min 0 sec
Transferring analysis options:  0 hr 0 min 0 sec
Total midsurf mapping:  0 hr 0 min 0 sec

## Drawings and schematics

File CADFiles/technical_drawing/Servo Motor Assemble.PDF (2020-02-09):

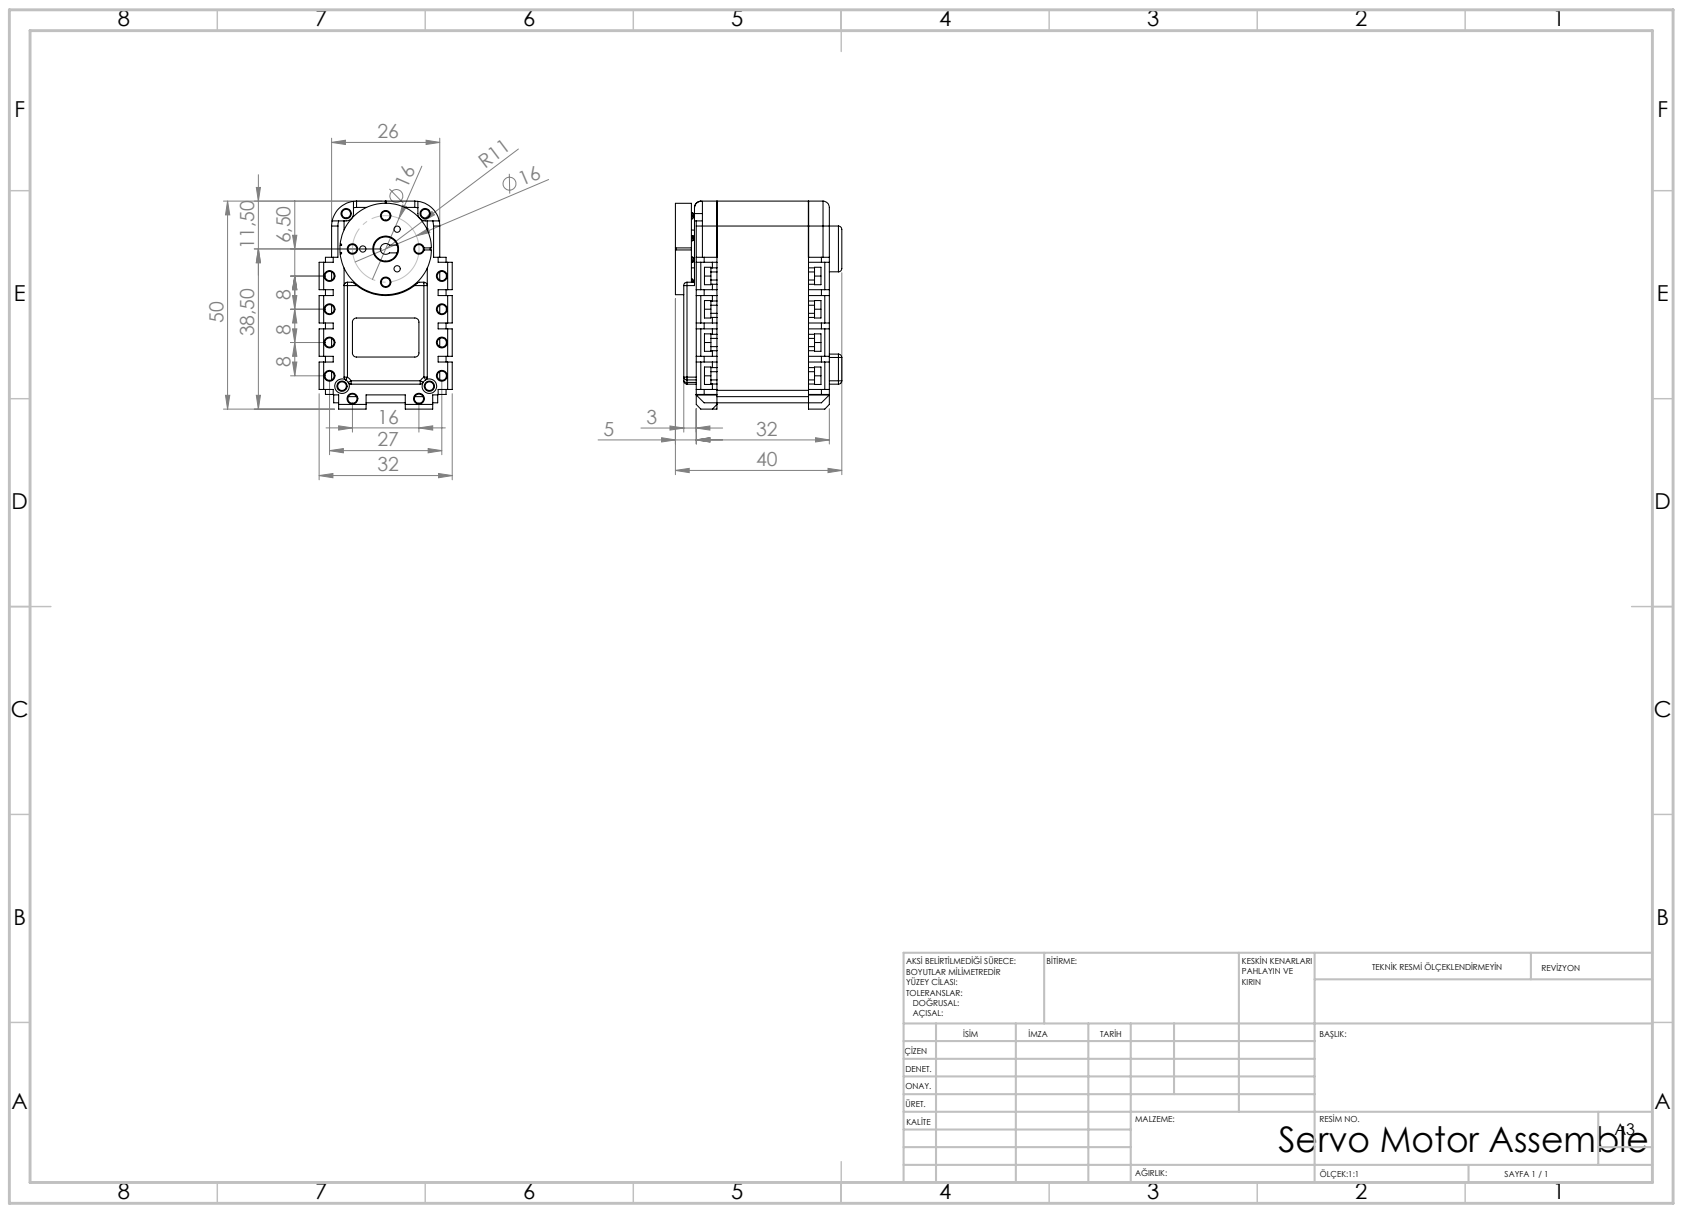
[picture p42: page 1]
BİTİRME:; KESKİN KENARLARI; PAHLAYIN VE; TEKNİK RESMİ ÖLÇEKLENDİRMEYİN; REVİZYON; ÖLÇEK:1:1; SAYFA 1 / 1

AKSİ BELİRTİLMEDİĞİ SÜRECE:
BOYUTLAR MİLİMETREDİR
YÜZEY CİLASI:
TOLERANSLAR:
DOĞRUSAL:
AÇISAL:

İSİM | İMZA | TARİH | | | | BAŞLIK:

ÇİZEN
DENET.
ONAY.
ÜRET.
KALİTE | | | | MALZEME: Servo Motor Assemble | RESİM NO. | A3

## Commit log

2019-12-24 Simulation files and videos were added.
    [MATLAB_feeding_robot_arm20.csv, first_link.STL, fourth_link.STL]
2020-02-09 CAD files, dynamic simulation files and report were added.
    [Servo Motor Assemble.SLDDRW, base_bowl_assemble.SLDASM, base_deneme.SLDPRT, base_plate.SLDDRW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]
